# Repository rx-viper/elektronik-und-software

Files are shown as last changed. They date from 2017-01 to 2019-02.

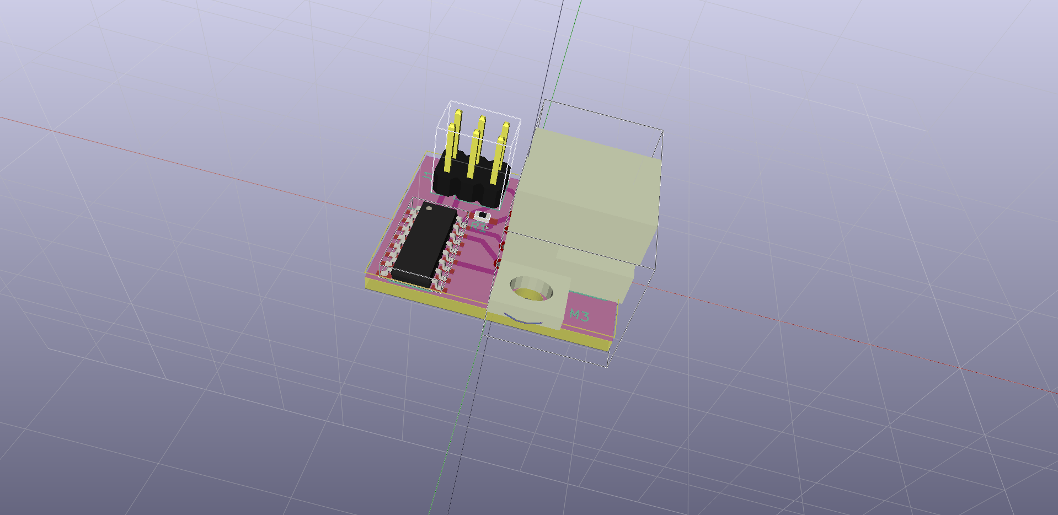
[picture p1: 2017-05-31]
boards/optical-distance/optical-distance.png

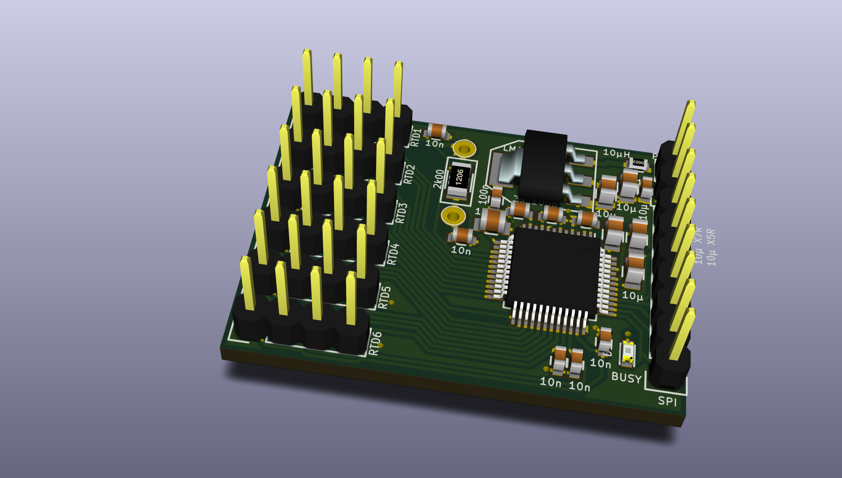
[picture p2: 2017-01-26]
docs/boards/temperature_sensor_board/ltc2984-board_3D_1.png

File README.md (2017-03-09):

# REXUS project VIPER: Elektronik and Software

### Structure of this repository

#### *boards*
* KiCAD and mechanical files for all PCBs used in the project.

#### *software/onboard*
* Code files of microcontroller software inside the rexus module.

#### *software/groundstation*
* Code files for the groundstation software (C++/Qt).

#### *docs*
* Documentation for all above.

### HowTo do changes to this repository

* Create a new branch: `git checkout -b feature/something-i-changed`
* Do your changes.
* Tell git what files your changed and want to commit: `git add my/file.changed my/other/file.changed`
* Commit your changes: `git commit -m "Description of my changes"`
* Push your changes to Github: `git push`
* Go to Github and create a new *Pull request* from your new branch to the *master* branch.
* Wait for someone to review and merge your Pull Request.
* Then checkout the *master* brach and pull the changes from Github: `git checkout master && git pull`

Use markdown syntax for text files and `*.md` file extension.

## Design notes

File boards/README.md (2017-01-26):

# rexus-viper-elektronik
Rexus Viper Elektronik Projekt

## Temperature Sensor Board
* LTC2984
* <-> 6x PT-100 4-wire
* -> 5V power supply
* <- SPI data out

## Mainboard
* -> Pressure sensor (SPI/I2C)
* -> Force sensor (analog/SPI/I2C)
* -> 5x Temperature sensor SPI (Temperature Sensor Board)
* -> Heat probe voltage and current sensing
* -> DS18B20 Temperature sensors (1-wire bus)
* 3.3V regulator
* STM32F429VI microcontroller
* Data storage (flash memory chip)
* <-> RXSM communication
* <- Raspberry Pi (UART)
* -> 5V power supply
* -> Status LEDs
* <- Control panel

## Powerboard
* -> Battery
* -> RXSM power
* 3x 60W 24V step-up converter
* <- Heat probe
* <- Motor power
* -> Motor control
* <- Battery heater
* <- Mainboard power
* <- Raspbery Pi power
* <- Camera power
* <- Camera light
* -> Camera control
* -> Heat probe control
* <- Heat probe voltage and current sensing

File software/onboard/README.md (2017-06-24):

## Onboard software

The main software is located in `src/`.
Any hardware component tests will be placed in `tests/`.

Board-specific configuration is done in `hardware_rev1.hpp` and is included from both main software and test software (`#include "../hardware_rev1.hpp` / `#include "../../hardware_rev1.hpp`).

## xpcc

To use this software you have to put a clone of the [xpcc git repository](https://github.com/roboterclubaachen/xpcc) in the same directory as this `rexus-viper-elektronik` repository.

## documentation
Documentation and flow charts can be found in docs/software/onboard folder.

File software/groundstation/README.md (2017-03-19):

## Groundstation software

#### documentation
Documentation, flow charts and and UI drafts can be found in  docs/software/groundstation folder.

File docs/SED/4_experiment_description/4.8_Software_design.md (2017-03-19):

 
## 4.8 Software design
 
### 4.8.1 Purpose
We use a Raspberry Pi compute module to handle the camera data and a powerful
microcontroller for data acquisition, experiment control and communication with RXSM.
All data shall be saved locally. Furthermore, all data except the camera data
shall be sent to ground station via RXSM.

### 4.8.2 Design
#### 4.8.2.1 Microcontroller
As you can see at the flowchart the main experiment control actions are triggered by the RXSM events.
Because of the different requirements about data acquisition we use different frequencycs for this. For details see data acquisition frequency table and data storage flowchart.
If we did not send any data in the past second, we will send an "alive" signal to check the connection state (especially for testing).
We will not control the heat probes to constant temperature, they will run on constant power, like couched at the requirements. In case of over temperature we will switch off the heat probes and switch on again with an hysteresis when cooled down enough.
Our software has a test mode, so the heat probes will not be activated while testing.
The uplink will only be used while testing to activate the test mode.
All data and also command and event log shall be sent to ground station via RXSM and be stored locally on a flash chip after LO.
For data package design see table xyz.

#### 4.8.2.2 Raspberry Pi 
The Raspberry Pi compute module, which handles the camera data, will remote controlled by the microcontroller.

#### 4.8.2.3 Groundstation
The groundstation software shall get the downstream from RXSM to store and visualize the data. 
It will have a easy to use GUI with a general log, where all incomming data will be logged and a critical log, to get a simple overview about critical events, like LO or problems like heat probe over temperature.
The GUI will visualize (in diagrams):
* the temperature distribution inside the ice cylinders
* the development of pressure
* the development of move distance and force of heat probes

It will display the connection status and will have a button to set the experiment in test mode.

### 4.8.3 Implementation
#### 4.8.3.1 Microcontroller
The microcontroller we want to use is a STM32 (see electronics). For development, we want to use C++ with the XPCC framework, it is very useful for hardware abstraction and parallelization and well known by Raphael Lehmann, who already contributed to XPCC.

#### 4.8.3.2 Raspberry Pi 
For the Raspberry Pi we want to use a minimized Linux, based on Raspbian. It will be remote controlled by the microcontroller via UART, so we don't need any complex software here.

#### 4.8.3.3 Groundstation
For the groundstation we will use C++ with QT library for graphical user interface.

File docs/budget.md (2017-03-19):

## Viper electronic budget

* Sensors
    * 100x Temperature sensor       7650..9900 €
    * 2x Pressure sensor            55 €
    * 6x Force sensor (Omega LCMKD) 3660 €
* Electronic components
    * Cameras
        * Visible light             150 €
        * IR                        250 €
    * 2x10x Batteries               80 €
    * Electronic components         1000 €
    * PCB's                         300 €
    * 2x Raspberry Pi CM3           60 €
    * Battery charger               60 €
    * Microcontroller programmer and logic analyzer 15 €
    * Cables                        150 €
    * Connectors                    350 €

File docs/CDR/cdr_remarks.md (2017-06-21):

## Electronics and SW Remarks form CDR discussion

* some double sentences and inconsistent sentences in SED
* some tbds inside SED
* some figures bottom lines are overlapping page numbers
* positioning of PCBs -> screw holes bulkhead
* we have to build boxes for every PCB, shielding very important
* no cables trough cupola wall - we need a vacuum approved connector
* RXSM connector has to be easily reachable and vertical oriented
* Simon: good schematics, could not find an error
* camera cables have to be as short as possible and shielded very well -> connect shielding to structure parts, not to PCBs GND
* some push buttons do wired things on rocket starts, select very careful
* filter motor control
* consider to use a save / arm plug for heaters
* onboard: RS-422; ground station: Rs-232
* STM should be able to check the camera status
* consider to start high frequency sampling before LO to be able to check it
* (software) test mode has to deal with LO - we will perform a full flight test at Esrange
* maybe send one timestamp at beginning and one at the end -> calculate timestamps later
* revise verification matrix software part
* batteries have to perform vacuum and vibration test
* calculate final number and power of batteries and add to SED
* batteries are a safety risk
* transportation of batteries from Esrange back is complicated
* consider check for late access status (lift mechanism really closed?)
* Esrange has a freezer for -80 deg - consider dry ice for transport, we will not be able to use our own sensors in freezer
* consider to change timeline to have more time for tests before LO
* what do we want to do in cold, what in hot CD tests?
* think about recovery -> anything special?
* error handling (flowcharts) for electrical / sw problems short before LO
* do electronics checks after switch to internal power
* for maximum packet size have a look at user manual

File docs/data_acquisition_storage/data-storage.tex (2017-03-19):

\documentclass[12pt, a4paper]{scrreprt}

\renewcommand{\familydefault}{\sfdefault}

\begin{document}

\subsubsection{Sensor data storage}
The initial idea was to store the sensor data with timestamps, but this has a few disadvantages.
\begin{itemize}
	\item Time resolution should be greater than $\frac{1}{50}s$, so we have to use milliseconds.
	\item Flight duration is 600s, but test may last longer.
	\item As a consequence 16bit timestamps are too short, we have to use 32bit timestamps (Our software framework \textit{xpcc} can handle both).
	\item A 32bit timestamp is bigger than the actual sensor data value, so it would increase the bandwidth and storage capacity by factor two to five.
	\item We don't have to store the time because we continuously sample all sensors.
\end{itemize}

\subsubsection{Solution}
\begin{itemize}
	\item Put multiple values from one unique sensor in a \textit{packet}, which also stores information about the sensor, its type and a sequence number.
	\item The packets can be used as buffers before sensor values are written to memory and transmitted.
\end{itemize}

\subsubsection{Sensor data packet}
\begin{tabular}{|c|c|c|c|}
	\hline 
	\multicolumn{3}{|c|}{\textbf{Header}} & \textbf{Payload} \\ 
	\hline 
	Sensor type & Sensor ID & Sequence Number  & Sensor values \\ 
	\hline 
	$2\,bit$ & $6\,bit$ & $4\,Byte$ & $123\,Byte$ \\ 
	\hline 
	\multicolumn{4}{|c|}{\textbf{Total packet size: 128 Byte}} \\ 
	\hline 
\end{tabular} 

\end{document}

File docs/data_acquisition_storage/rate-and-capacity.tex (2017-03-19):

\documentclass[12pt, a4paper]{scrreprt}

\renewcommand{\familydefault}{\sfdefault}

\begin{document}

\begin{tabular}{|c|c|c|c|c|}
	\hline 
	Sensor & Count & Frequency / $Hz$ & Resolution / $Byte$ & Data rate / $B/s$ \\ 
	\hline 
	Ice temperature & 27 & 1.5 & 3 & 121.5 \\ 
	\hline 
	Other temperature & 5 & $\frac{1}{10}$ & 2 & 1 \\ 
	\hline 
	HPPM force & 3 & 2 & 3 & 18 \\ 
	\hline 
	Pressure & 1 & 20 & 2 & 40 \\ 
	\hline 
	Heat probe temperature & 3 & 1.5 & 3 & 13.5 \\ 
	\hline 
	\textbf{Total} & 39 & & & 194 \\ 
	\hline 
\end{tabular} 
\\[0.5em]
Experiment duration: $120\,s \rightarrow 194B/s * 120s = 23.28kB$
\\[0.5em]
Flight duration: $600\,s \rightarrow 194B/s * 600s = 116.4kB$

\end{document}

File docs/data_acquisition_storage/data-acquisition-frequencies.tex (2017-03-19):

\documentclass[12pt, a4paper]{scrreprt}

\renewcommand{\familydefault}{\sfdefault}

\begin{document}

\begin{tabular}{|c|c|c|}
	\hline 
	Sensor & Low frequency & High frequency \\ 
	\hline 
	Ice temperature & $\frac{1}{3}\,Hz$ & $1.5\,Hz$ \\ 
	\hline 
	Battery/Structure temperature & $\frac{1}{10}\,Hz$ & $\frac{1}{5}\,Hz$ \\ 
	\hline 
	HPPM force & disabled & $2\,Hz$ \\ 
	\hline 
	Pressure & $5\,Hz$ & $20\,Hz$ \\ 
	\hline 
	Heat probe temperature & disabled & $1.5\,Hz$ \\ 
	\hline 
\end{tabular}

\end{document}

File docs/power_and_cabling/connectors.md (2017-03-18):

# Connectors

## List of connectors in experiment

**Where | type | number of pins | necessary**
* ISCA temperature sensors to mainboard | 2x D-SUB HD (44 + 62 pin) | 27x4 (=108), but each 6 sensors share 1 pin -> 86 pins | yes
* RXSM connector | DSUB-15 | 15 | yes
* Battery connector to powerboard | no? | 2x high-current + temperature sensors (5) | we could solder the battery to the powerboard
* powerboard to mainboard | D-SUB (HD?) 26 or 37 pin | about 20 | yes
* Coupola (sensors) to mainboard | D-SUB (HD?) | approx. 15 pins | yes
* Coupola (cameras) to Raspberry Pi CM3 board | D-SUB (HD?) | <=15 | yes
* Coupola (heat probes, light) to powerboard | D-SUB (?), multiple pins parallel | 6x high-current, 2x light | yes

## Available connectors

* D-SUB HD (high density) 15..78 pins; [Harting](http://www.harting.de/fileadmin/harting/documents/public/catalogue/interface_11_7_d/Interface_11_7_D_03_D-Sub-High-Density-Steckverbinder.pdf)
* D-SUB 9..50 pins
* high current: D-SUB multiple pins parallel

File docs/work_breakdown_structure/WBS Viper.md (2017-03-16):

* Specify hardware design
    * Sensors
    * Actuators
    * Batteries
    * Processing units
    * Data acquisition
    * Developing schematics
        * Calculate
        * Draw
* Specify software design
    * Requirements
    * Flow charts
* Select parts
* Develop hardware
    * Design board layouts
* Develop software
    * Ground Station
        * Telemetry data
            * Store
            * Process
            * Visualize
        * Telecommand
    * Onboard
        * Process ground commands
        * Control
            * Actuators
                * Range limit
            * Heat probes
                * Over-heating protection
            * Locking mechanism
            * Start/Stop experiment/data acquisition
            * Camera
        * Data management
            * Read sensor data
            * Store data
            * Pack and format data
            * Send to RXSM for transmission
* Assemble hardware
    * Assemble boards
    * Assemble cables
* Testing hardware components
    * Sensors
        * Temperature
        * Pressure
        * Force
        * Camera
    * Batteries
        * Vacuum
        * Temperature development under load
        * Capacity under load
        * Voltage, current at different temperatures
    * Actuators
        * Motor
        * Heat probes
* Final Assembly
    * Temperature sensors
    * Wiring
    * Adjust camera
* Final testing

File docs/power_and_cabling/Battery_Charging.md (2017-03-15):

# Battery charging

We use a 8 cell NiMH battery inside our module.

The battery is charged inside the experiment module through the RXSM charge line, which provides 1A at 28V. Our Battery is charged with 20W.

The battery charge controller is integrated to the *Powerboard* and can be enabled from the Mainboards microcontroller.
A charge status feedback is provided to the microcontroller, too.

For efficiency reasons we use the [Linear LTC4010](http://www.linear.com/product/LTC4010) *High Efficiency Standalone Nickel Battery Charger*. This integrated circuit provides reliable and safe battery charging with only a few additional components.

### Charge current
The charge current is set to 2A according to the [LTC4010s datasheet](http://cds.linear.com/docs/en/datasheet/4010fb.pdf).
```
R_sense = 100mV / I_charge
0.05 ohms = 100mV / 2A
```

### Battery cut-off
The battery is always disconnected from the load while RXSM power is not available.
For technical reasons the charging circuit is not disconnected, but is only enabled and active while the RXSM charge line is powered.
To charge the battery both RXSM power line and charge line have to be powered on because the microcontroller must enable the battery charging circuit.

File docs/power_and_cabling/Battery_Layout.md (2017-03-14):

# Battery Power and Energy Calculation
```
Heatprobes:     P = 35W + 70W + 70W + 5W margin = 180W
                U = 24V
Experiment:     t = 3min = 180s = 0,05h
Efficienty:     Step Up = 0,93
BK250 SCH       Q = 2800mAh
                m = 57g
```				
## Calculation:
```			
                    Conversation losses: 180W * 0,07 = 12,6W
                    E_Heatprobe = 180W * 0,05h = 9Wh
                    E_Cell = 1,2V * 2800mAh = 3,36Wh per Cell
                    E_Waste = 12,6W * 0,05h = 0,63Wh
                    E_total = 9Wh + 0,63Wh = 9,63Wh
    Amount Cells:   E_total/E_Cell = 9,63Wh/3,36Wh = 2,866 Cells
                    => 3 Cells

    1,1V at 20A     P_Cell = 1,1V * 20A = 22W
    (Batterychart)  P_Heatprobe = 180W
                    P_Loss = 12,6W
                    P_Total = P_Heatprobe + P_Waste = 180W + 12,6W = 192,6W
    Amount Cells:   P_Total/P_Cells = 192,6W/22W = 8,75 Cells
                    => 9 Cells

    1,0V at 30A     P_Cell = 1,0V * 30A = 30W
    (Batterychart)  P_Heatprobe = 180W
                    P_Waste = 12,6W
                    P_Total = 192,6W
    Amount Cells:   P_Total/P_Cells = 192,6W/30W = 6,41 Cells
                    => 7 Cells

    => Amount Cells chosen: 8 Cells
```

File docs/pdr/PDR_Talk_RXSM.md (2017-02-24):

## RXSM

### Telemetry
* `19.2 kbit/s` shared
* Ground station (GS) is connected to *SCIENCE-NET*
    * via RS232
    * **or:** direct TCP connection to a dedicted port at serial port server
    * we should implement both, RS232 as falllback
* Telemetry has forward error correction (FEC)
* Telemetry imput: raw serial datastream via RS422
* <64 bytes at a time
* fragmentation -> delay up to ~4ms
* RS422 termination resistor

### Signals
* LO: lift off (fixed, shared for all experiments)
* SOE: start of experiment
* SODS: start of data storage
* SOE, SODS programmable via timeline after liftoff
* SOE, SODS manually activatable before LO
* open collector
    * shared: diode decoupled
    * "active low"
    * max. 50mA
    * unstable after power on -> wait 5 seconds after power on
    * glitches are possible -> debouncing
    * use optocoupler, no anitparallel diode, e.g. PC3H7, connect direct to 28V line
* we need a special rundown sequence because of mechanical state

### Uplink
* only available before LO on RX23 (our rocket)
* use for testing, etc.

## RXSM Power
* resetable fuses in RXSM
    * >3A for >500ms
    * >15A for >10ms
    * -> no own fuses
* max. ripple voltage: 100mV_pp
* 28V nominal voltage
    * on ground: regulated 28V power supply, but long wires -> high inductance
    * during flight: unregulated battery voltage
    * total range: 24V to 36V
* provide good access to power connectors!
* power input:
    * <100µF input capacity
    * EMI supression input filter
    * 100nF at input after filter
    * GND shorted to structure only at one input point

## Cables
* 4A / mm²

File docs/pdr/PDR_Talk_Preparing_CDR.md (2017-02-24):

## CDR
* final design!
* 20 minutes presentation
* SED deadline: 22/05
* Soldering course (?)

### How to prepare:
* Use PDR feedback
* Ask! (Mail, Telefone)
* RTFM!!!

### Electronics:
* schematics
* pcb (layouts)
* Cabling!
* everything tested

### Software:
* testing subsystems
* ground station
* software responsible person must be at CDR

### Handling:
* Storage space -> read data and clear flash?

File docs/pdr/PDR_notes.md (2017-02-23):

* LO, SOE, SODS signal
* Termination resistor
* Galvanic isolation
* Battery charging through RXSM charge line
* Battery cut-off
* Late access procedure (radio silence / no power)
    * -> no LEDs
* Camera
    * EMV
    * Don*t use CSI connectors from RPi camera
    * Camera lens heater

* SED:
    * We will use LaTeX
    * verifcation is missing
    * Software Design in SED
    * Citations in SED

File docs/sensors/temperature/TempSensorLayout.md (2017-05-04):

# Configuration temperature sensors

## Calculation of accuracy

Requirements:
```
dT = 0.5°C in a range of -80°C to 0°C
dT = 0.1°C in a range of -80°C to 0°C if possible
```

#### Class B
```
dT = ± (0.30°C + 0.005 * |T|)
dT = ± (0.7°C)
```

#### Class A
```
dT = ± (0.15°C + 0.002 * |T|)
dT = ± (0.31°C)
```

#### Class AA
```
dT = ± (0.10°C + 0.0017 * |T|)
dT = ± (0.236°C)
```

#### Class 1/10 B
```
dT = ± (0.1*(0.30°C + 0.005 * |T|)
dT = ± (0.07°C)
```

=> Class A and AA fulfill the requirement, Class 1/10 B would be great

### Quantity
* 9 sensors per iceblock
* 27 sensors per ISCA
* We have two ISCAs in reserve, one for the flight. 
* 81 sensors are necessary
    * We will order 100 sensors, 81 mounted, 19 for testing and replacement

### Costs

Sensors by Omega can be custom made.
A sensor that might fit would be *P-M-1/10-2-5-M6x1* for 99€ each.

This sensor and alternatives will be discussed (PT100; 1/10 Class B; 2mm diameter; 5mm length; M6-1 screw mount).

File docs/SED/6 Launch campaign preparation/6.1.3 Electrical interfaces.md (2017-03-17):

### 6.1.3 Electrical Interfaces
#### REXUS Electrical Interfaces
* Service module interface required? Yes
    * Number of service module interfaces: 1
    * TV channel required?: No
* Downlink required? Yes
    * Data rate downlink: 20 kbit/s
* Uplink required? Yes, but only on ground
    * Data rate uplink: < 1 kbit/s
* Power system: Service module power required? Yes
    * Peak power consumption: 30 W
    * Average power consumption: 10 W
    * Total power consumption after lift-off (until T+600s): 1.67 Wh
    * Power ON: 600 s before lift-off
    * Power OFF: 600 s after lift-off
    * Battery recharging through service module: Yes
* Experiment signals: Signals from service module required? Yes
    * LO: Yes
    * SOE enable: 80 s after lift-off (begin of µg-phase)
    * SOE disable: 200 s after lift-off (end of µg-phase)
    * SODS enable: 300 s before lift-off
    * SODS disable: 550 s after lift-off (50 s before shut-down)

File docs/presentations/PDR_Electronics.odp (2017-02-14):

## Electronics

## Overview

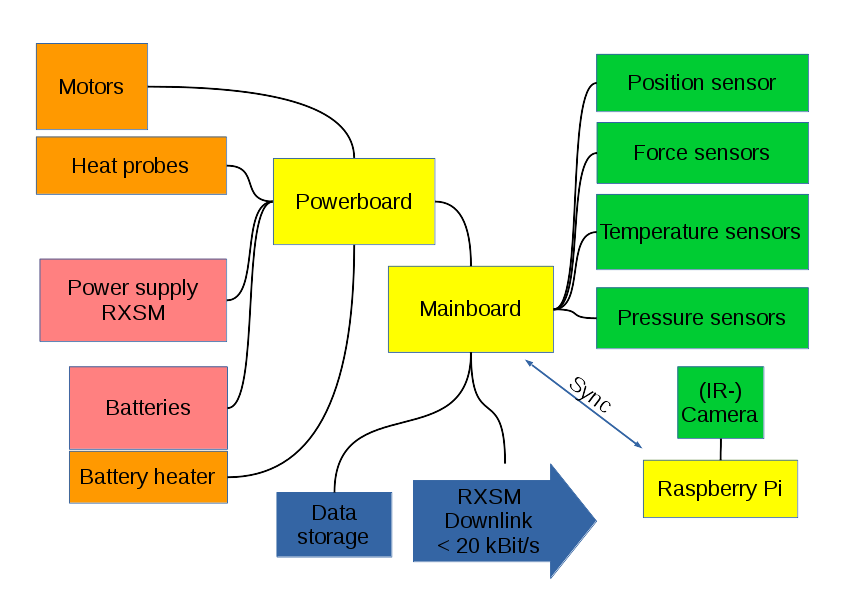
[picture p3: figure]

## Battery

- Panasonic BK300SCP
  - NiMH
  - 1.2 V
  - 3 Ah
  - 4 mΩ
- 8..10 cells
- 25..35 Wh
- Temperature monitoring
- Battery heater

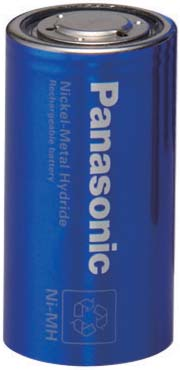
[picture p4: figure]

## Temperature Sensor Board

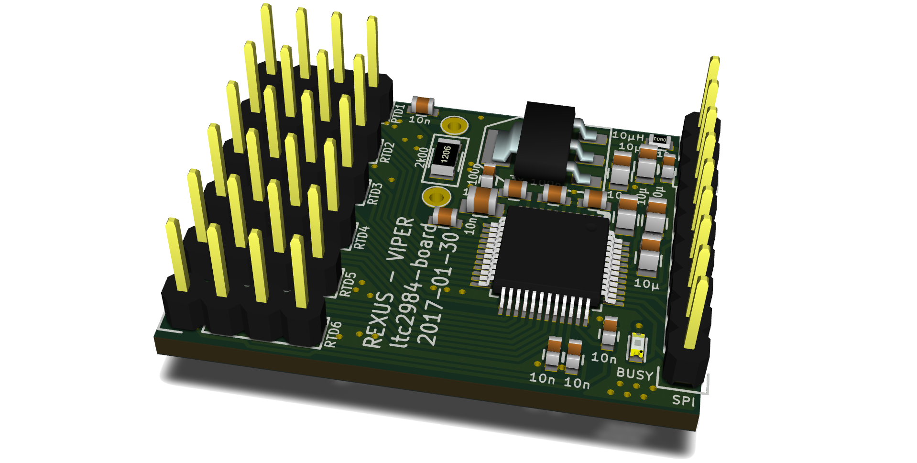
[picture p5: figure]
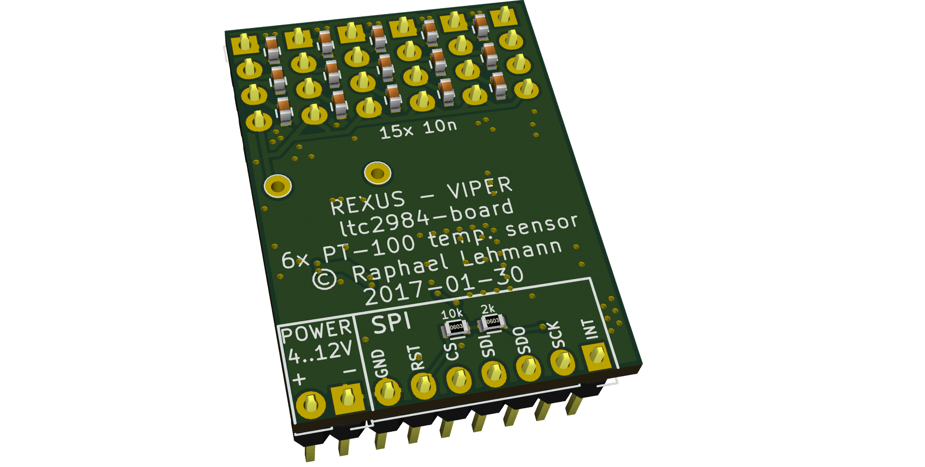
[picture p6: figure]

## Boost regulator test board

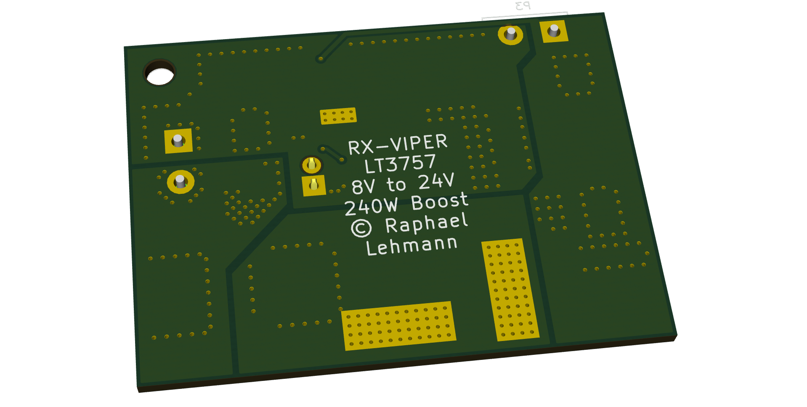
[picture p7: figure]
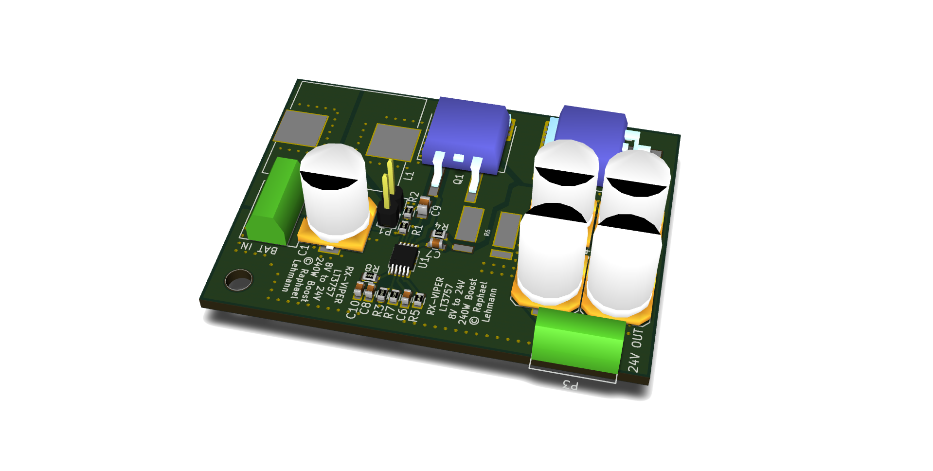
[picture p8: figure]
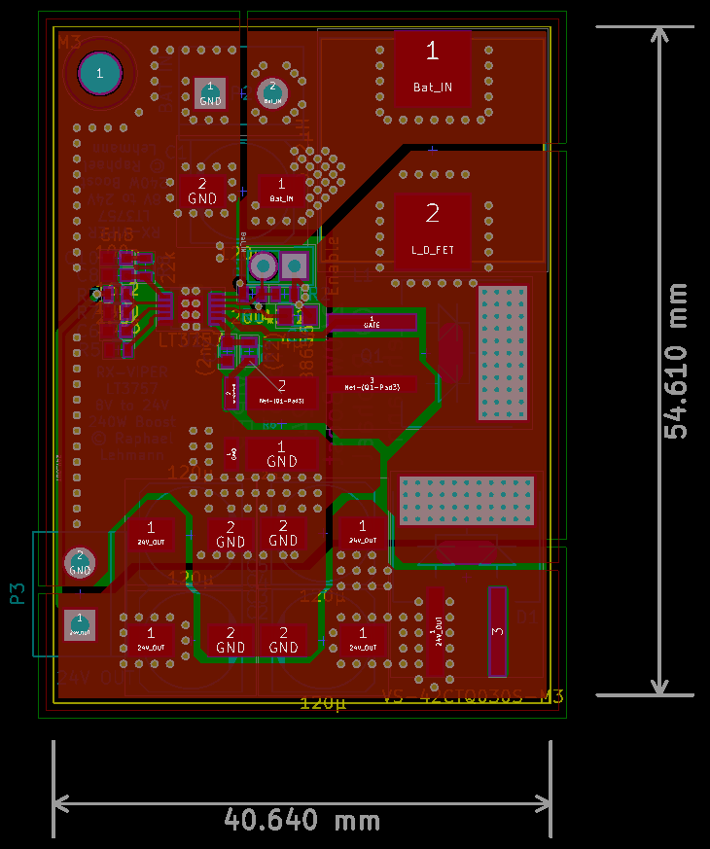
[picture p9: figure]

## Software Design

## Onboard Software

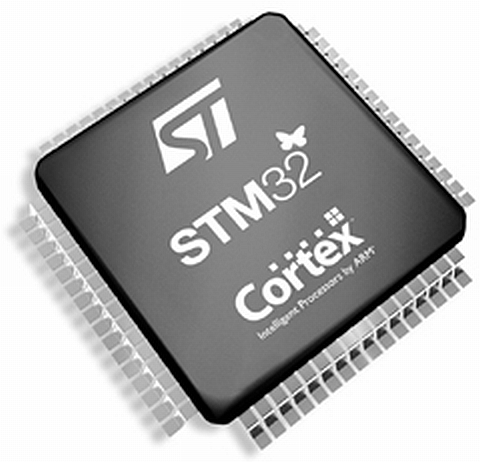
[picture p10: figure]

- STM32 microcontroller
- xpcc framework
  - C++
  Raspberry Pi: Linux
  Communication:
- xpcc
- Experiment ↔ ground station

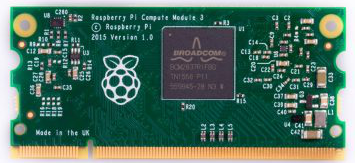
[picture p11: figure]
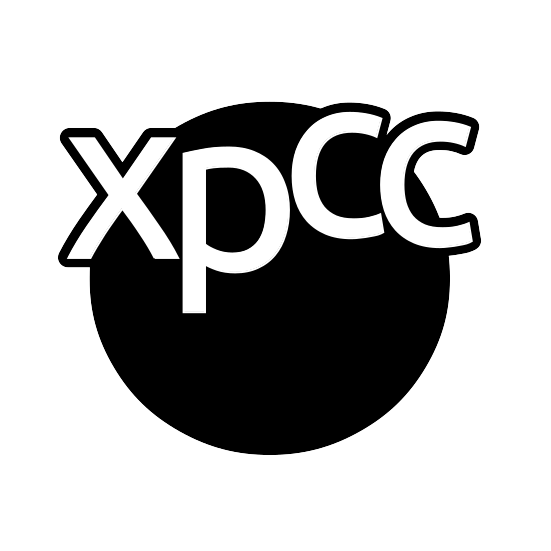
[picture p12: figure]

## Software Flowchart

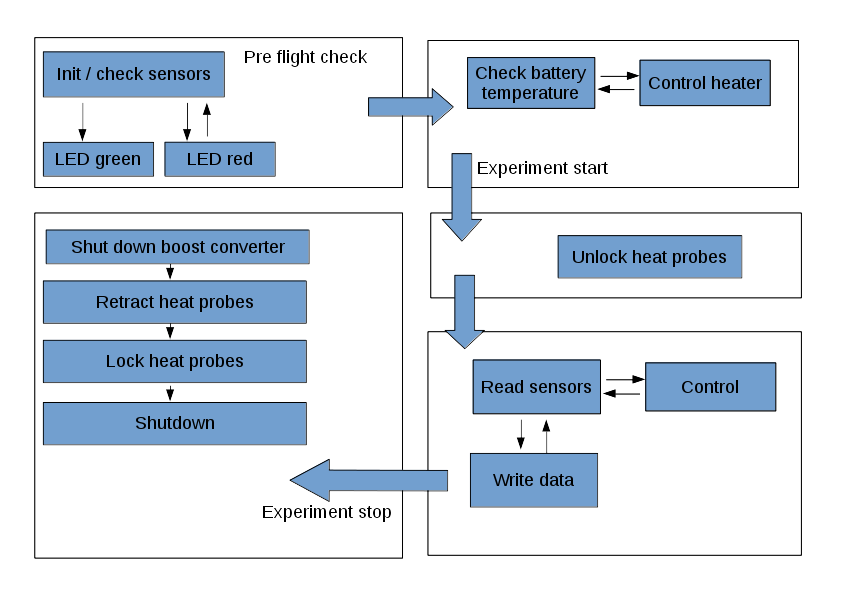
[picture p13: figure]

## Ground Station

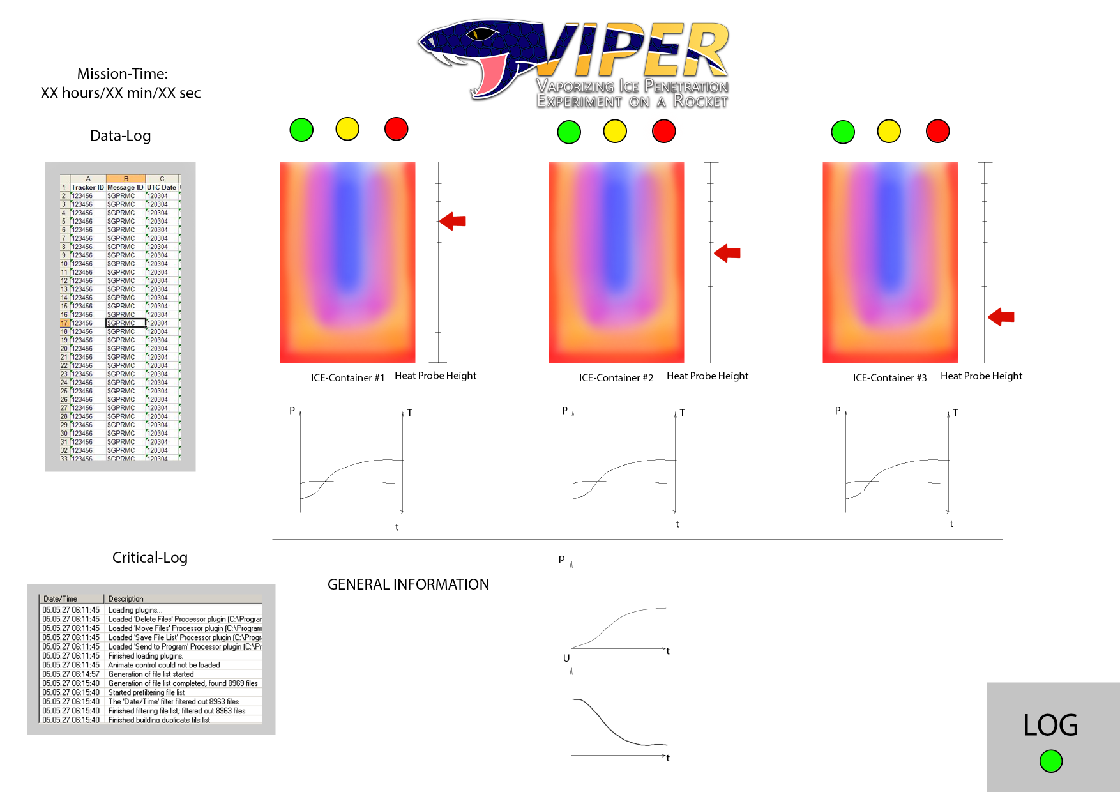
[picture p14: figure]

- Experiment status overview
- Record received data
- Qt GUI (C++)

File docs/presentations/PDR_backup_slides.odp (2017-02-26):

## Pressure sensor

- AMS 5915-0010-D
- I²C
- differential, 0..10mbar
- temperature compensated -25..85°C
- available, 25€

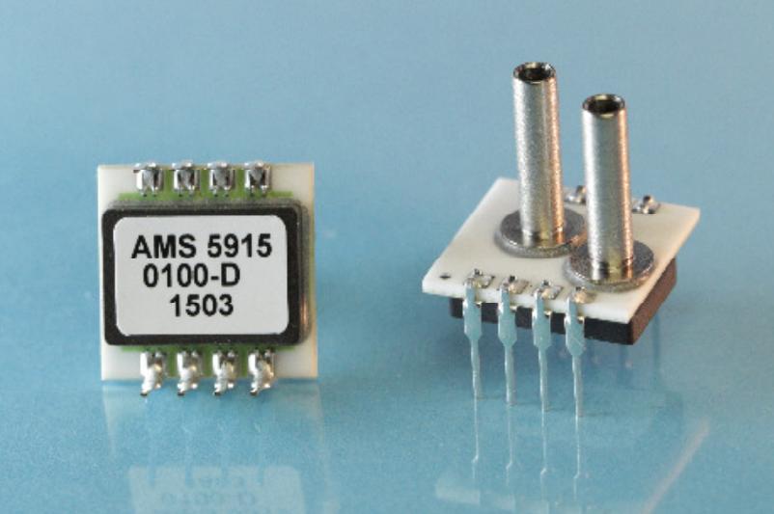
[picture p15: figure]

## Temperature sensing

- Requirement
  - Accuracy 0.5% or better
  - Range: -100°C .. 20°C
- PT-100
- LTC2984 integrated temperature measurement system
- 4-wire connections

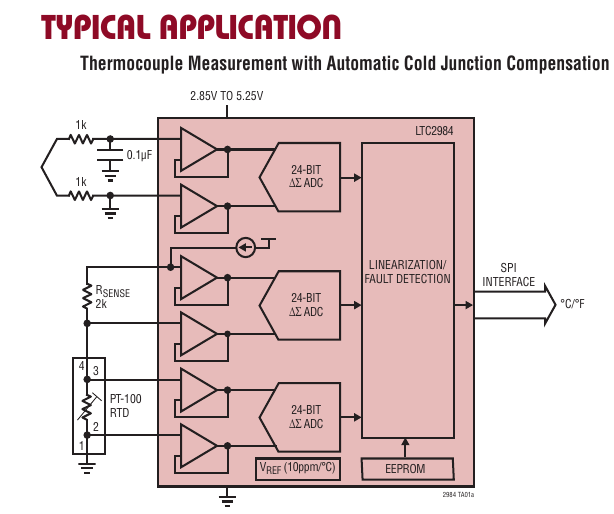
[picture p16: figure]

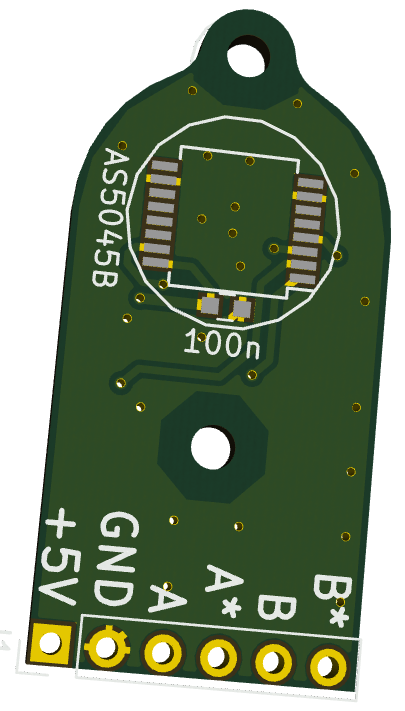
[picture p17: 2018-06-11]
docs/boards/Cupola-Boards/Renderings/Encoder-Board-VarA_Back.png

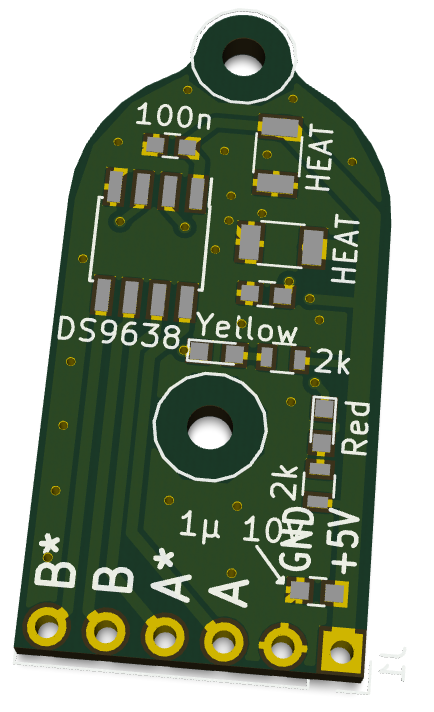
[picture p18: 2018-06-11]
docs/boards/Cupola-Boards/Renderings/Encoder-Board-VarA_Front.png

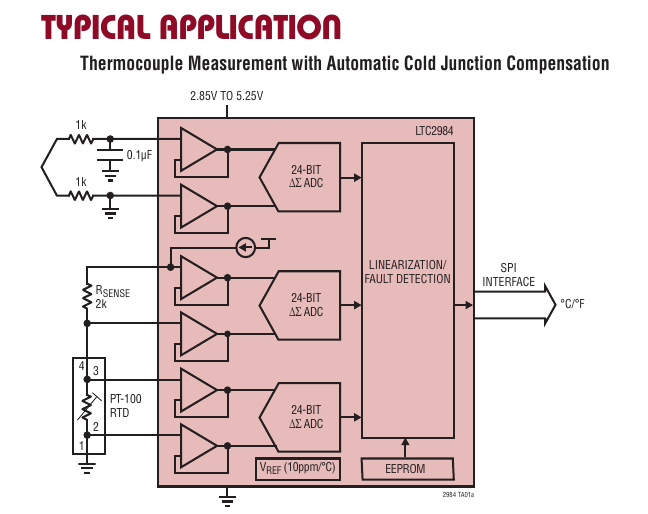
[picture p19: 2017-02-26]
docs/presentations/ltc2984-example.png

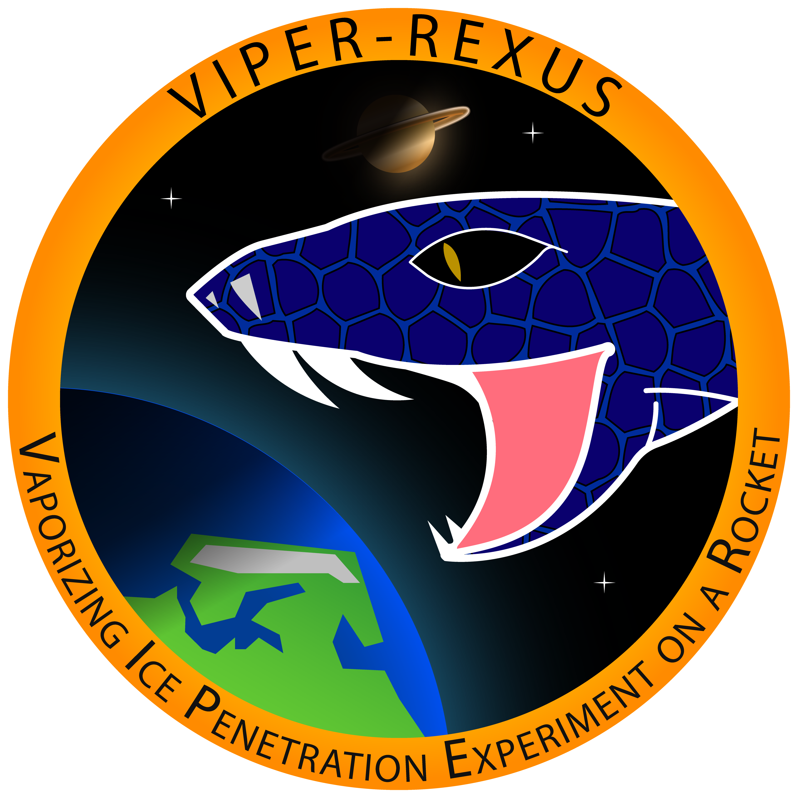
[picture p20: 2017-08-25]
docs/wires/VIPEREmblemTransparent.png

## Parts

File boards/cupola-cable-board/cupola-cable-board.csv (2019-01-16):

ID | Bezeichner | Gehäuse | Stückzahl | Bezeichnung | Anbieter und Referenz
1 | IC2,IC1 | SOIC-16_3.9x9.9mm_P1.27mm | 2 | AM26C31M
2 | J3 | PinHeader_2x03_P2.00mm_Vertical | 1 | ENC1_OUT
3 | J2 | PinHeader_2x03_P2.00mm_Vertical | 1 | ENC0_OUT
4 | J4 | PinHeader_2x03_P2.00mm_Vertical | 1 | ENC2_OUT
5 | C9,C4,C8,C10,C3,C5,C6,C11 | C_0603_1608Metric | 8 | 100n
6 | X1 | Oscillator_SMD_SeikoEpson_SG8002LB-4Pin_5.0x3.2mm | 1 | ECS-3963-120-AU-TR
7 | TP3,TP1,TP2 | TestPoint_Pad_D1.5mm | 3 | TestPoint
8 | R8,R6,R5 | R_0805_2012Metric | 3 | HEAT
9 | J5 | PinHeader_1x06_P2.00mm_Vertical | 1 | Sensor0
10 | J10 | PinHeader_1x04_P2.00mm_Vertical | 1 | MagnetEncoder2
11 | J1 | PinHeader_1x02_P2.00mm_Vertical | 1 | LED
12 | J9 | PinHeader_1x04_P2.00mm_Vertical | 1 | MagnetEncoder1
13 | J8 | PinHeader_1x04_P2.00mm_Vertical | 1 | MagnetEncoder0
14 | J7 | PinHeader_1x06_P2.00mm_Vertical | 1 | Sensor2
15 | J6 | PinHeader_1x06_P2.00mm_Vertical | 1 | Sensor1
16 | JP2 | SolderJumper-3_P1.3mm_Open_RoundedPad1.0x1.5mm | 1 | Enc0_B
17 | C2,C12,C13,C1 | C_0603_1608Metric | 4 | 1u
18 | C7 | C_0805_2012Metric | 1 | 4u7
19 | J11 | PinHeader_1x03_P2.54mm_Vertical | 1 | SWD
20 | JP1 | SolderJumper-3_P1.3mm_Open_RoundedPad1.0x1.5mm | 1 | Enc0_A
21 | JP3 | SolderJumper-3_P1.3mm_Open_RoundedPad1.0x1.5mm | 1 | Enc1_A
22 | JP4 | SolderJumper-3_P1.3mm_Open_RoundedPad1.0x1.5mm | 1 | Enc1_B
23 | JP5 | SolderJumper-3_P1.3mm_Open_RoundedPad1.0x1.5mm | 1 | Enc2_A
24 | JP6 | SolderJumper-3_P1.3mm_Open_RoundedPad1.0x1.5mm | 1 | Enc2_B
25 | U2 | LQFP-48_7x7mm_P0.5mm | 1 | STM32F410CBTx
26 | U1,U3 | SOT-23-5 | 2 | TLV75533PDBV
27 | R7,R1 | R_0603_1608Metric | 2 | 0
28 | R2,R3,R4 | R_0603_1608Metric | 3 | 3k3
29 | D1,D2,D3 | LW_G6SP_Handsoldering | 3 | LED

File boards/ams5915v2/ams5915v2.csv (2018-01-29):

Id | Designator | Package | Quantity | Designation | Supplier and ref | partsbox
1 | REF**,REF**,REF** | MountingHole_3.2mm_M3 | 3 | MountingHole_3.2mm_M3 |  | n
2 | C1,C7,C8 | C_0805 | 3 | 1u |  | x
3 | C2 | C_1206 | 1 | 10u |  | x
4 | C3,C4,C5,C6 | C_0603 | 4 | 100n |  | x
5 | D1 | LED_0603 | 1 | LED_5v |  | x | green
6 | D2 | LED_0603 | 1 | LED_3v3 |  | x | yellow
7 | D3 | LED_0603 | 1 | LED_P1 |  | x | red
8 | D4 | LED_0603 | 1 | LED_P2 |  | x | red
9 | J1 | Pin_Header_Angled_1x04_Pitch2.54mm | 1 | Conn_01x04 |  | n
10 | R1,R2 | R_0603 | 2 | 100 |  | x | Zero-ohm
11 | R3 | R_0603 | 1 | 4k7 |  | x
12 | R4,R6,R8 | R_0603 | 3 | 2k7 |  | x
13 | R5,R7 | R_0603 | 2 | 576k |  | x
14 | TP2 | Measurement_Point_Round-SMD-Pad_Small | 1 | GND |  | n
15 | TP3 | Measurement_Point_Round-SMD-Pad_Small | 1 | 3v3 |  | n
16 | U1 | SOT-23-5 | 1 | TLV73333PDBVR |  | x
17 | U2,U4 | SOT-23-6 | 2 | MAX4995A |  | x
18 | U3,U5 | AMS_5915-XXXX-D_differential_pressure_sensor | 2 | AMS5915 |  | x
19 | TP1 | Measurement_Point_Round-SMD-Pad_Small | 1 | 5v |  | n

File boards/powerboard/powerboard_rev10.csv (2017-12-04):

ID | Bezeichner | Gehäuse | Stückzahl | Bezeichnung | Anbieter und Ref. | partsbox
1 | J113,J112,J113,J114,J115,J117 | MountingHole_3.2mm_M3_Pad | 6 | M3 |  | n
2 | C503 | C_0805 | 1 | 10µ 0805 35V |  | 1 | 0
3 | FL101,FL102 | WE-SL5 | 2 | 744272471 |  | 2 | 0
4 | C104,C505 | C_0805 | 2 | 10µ |  | 2 | 0
5 | C105,C304,C305,C308,C309,C310,C312,C315,C504,C701,C801,C802,C803,C901,C902,C1002,C109,C506,C1201,C1202,C302,C306 | C_0603 | 22 | 100n |  | 22 | 0
6 | C106 | C_0805 | 1 | 470n |  | 1 | 0
7 | C201 | C_1206 | 1 | 10µ/40V |  | 1 | 0
8 | C202 | C_0805 | 1 | 1µ/40V |  | 1 | 0
9 | C203,C204 | C_0603 | 2 | 22n |  | 2 | 0
10 | C205,C110,C111,C112,C113,C114,C115,C116,C117,C910,C911,C912,C913,C914,C915,C916,C917 | C_0603 | 17 | 10n |  | 17 | 0
11 | C303 | C_0603 | 1 | 10µ |  | 1 | 0
12 | C307,C314,C702,C1001,C207 | C_0603 | 5 | 1µ |  | 5 | 0
13 | C313 | C_0603 | 1 | 4µ7 0805 |  | 1 | 0
14 | C316,C317,C318 | C_0603 | 3 | 100p |  | 3 | 0
15 | C501 | C_0603 | 1 | 68n |  | 1 | 0
16 | C502 | C_0603 | 1 | 47n |  | 1 | 0
17 | C1101,C1102,C1103,C1104,C1105,C1106,C1107,C1108,C1109,C1110,C1111,C1112,C1113,C1114,C1115,C1116,C508 | C_0603 | 17 | 220n |  | 17 | 0
18 | D301,D302 | LED_0603 | 2 | LED |  | 2 | 0
19 | D701,D702 | SOT-23 | 2 | ESD |  | 2 | 0
20 | J102 | Pin_Header_Straight_2x20_Pitch2.54mm | 1 | Powerboard <-> Mainboard |  | 0 | 1
21 | J105 | MountingHole_3.2mm_M3_Pad_Via | 1 | BOOST |  | 0 | 1
22 | J106 | Pin_Header_Straight_1x01_Pitch2.54mm | 1 | Boost24V_EN |  | 0 | 1
23 | J107 | MountingHole_3.2mm_M3_Pad_Via | 1 | 24V_1 |  | 0 | 1
24 | J108 | MountingHole_3.2mm_M3_Pad_Via | 1 | 24V_2 |  | 0 | 1
25 | J109 | MountingHole_3.2mm_M3_Pad_Via | 1 | 24V_3 |  | 0 | 1
26 | J110 | MountingHole_3.2mm_M3_Pad_Via | 1 | BAT |  | 0 | 1
27 | J111 | MountingHole_3.2mm_M3_Pad_Via | 1 | GND |  | 0 | 1
28 | L301,L302,L303 | L_1812 | 3 | 742792515 |  | 3 | 0
29 | Q101 | TO-263-3Lead | 1 | SQM40031EL |  | 1 | 0
30 | Q102 | SOT-23 | 1 | DMN6140L |  | 1 | 0
31 | Q104 | SOT-23 | 1 | PMV55ENEA |  | 1 | 0
32 | Q503 | SOIC-8_3.9x4.9mm_Pitch1.27mm | 1 | IRF7343PBF |  | 1 | 0
33 | Q801,Q802,Q803 | SOT-669_LFPAK | 3 | BUK7Y4R8-60E |  | 3 | 0
34 | R101,R103,R801,R802,R803,R125,R126,R807,R808,R809,R508,R123,R124,R128 | R_0603 | 14 | 10k |  | 14 | 0
35 | R102 | R_0603 | 1 | 20k |  | 1 | 0
36 | R104 | R_0603 | 1 | 91k |  | 1 | 0
37 | R105 | R_0603 | 1 | 13k |  | 1 | 0
38 | R106,R108,R113 | R_0603 | 3 | 15k |  | 3 | 0
39 | R107,R109,R110,R111,R114,R607,R608,R130 | R_0603 | 8 | 1k |  | 8 | 0
40 | R112,R1002,R129 | R_0603 | 3 | 100k |  | 3 | 0
41 | R201 | R_0603 | 1 | 68k1 |  | 1 | 0
42 | R202 | R_0603 | 1 | 11k8 |  | 1 | 0
43 | R203 | R_0603 | 1 | 43k2 |  | 1 | 0
44 | R204 | R_0603 | 1 | 5k62 |  | 1 | 0
45 | R205 | R_0603 | 1 | 1k07 |  | 1 | 0
46 | R301,R302 | R_0603 | 2 | 470 |  | 2 | 0
47 | R303 | R_0603 | 1 | 200k |  | 1 | 0
48 | R504 | R_0603 | 1 | 65k7 |  | 1 | 0
49 | R505 | R_0603 | 1 | 8k2 |  | 1 | 0
50 | R506 | R_0603 | 1 | 50k |  | 1 | 0
51 | R1001 | R_0603 | 1 | 140k |  | 1 | 0
52 | R1003 | R_0603 | 1 | 4k7 |  | 1 | 0
53 | R1004 | R_0603 | 1 | 2R |  | 1 | 0
54 | R1101,R1102,R1103,R1104,R1105,R1106,R1107,R1108,R1109,R1110,R1111,R1112,R1113,R1114,R1115,R1116 | R_0603 | 16 | 47k |  | 16 | 0
55 | U102 | SOIC-16_3.9x9.9mm_Pitch1.27mm | 1 | DS26LV32AT |  | 1 | 0
56 | U201 | 7TO-PMOD | 1 | LMZ14203 |  | 1 | 0
57 | U302 | HSSOP-36 | 1 | DRV8332 |  | 1 | 0
58 | U303,U801,U802,U803 | SOIC-8_3.9x4.9mm_Pitch1.27mm | 4 | ACS711 |  | 4 | 0
59 | U501 | TSSOP-16-1EP_4.4x5mm_Pitch0.65mm | 1 | LTC4010 |  | 1 | 0
60 | U601,U602,U603 | SOP-4 | 3 | PC3H7 |  | 3 | 0
61 | U701 | SOIC-14_3.9x8.7mm_Pitch1.27mm | 1 | MAX13432EESD |  | 1 | 0
62 | U901 | TSSOP-20_4.4x6.5mm_Pitch0.65mm | 1 | AD7928 |  | 1 | 0
63 | U902 | SOT-23 | 1 | REF3025 |  | 1 | 0
64 | U1001 | MSOP-10-1EP_3x3mm_Pitch0.5mm | 1 | LT3592 |  | 1 | 0
65 | U1101,U1102 | TSSOP-14_4.4x5mm_Pitch0.65mm | 2 | LMV324 |  | 2 | 0
66 | C103 | C_0805 | 1 | 1µ |  | 1 | 0
67 | L101 | L_Coilcraft_1583_Handsoldering | 1 | Coilcraft MSS1583-474 |  | 1 | 0
68 | L501 | L_Coilcraft_XAL60xx_Handsoldering | 1 | Coilcraft XAL6060-223 |  | 1 | 0
69 | L1001 | L_Coilcraft_XAL40xx_Handsoldering | 1 | Coilcraft XAL4040-103 |  | 1 | 0
70 | U101 | SOT-223 | 1 | LM1117-3.3 |  | 1 | 0
71 | R115,R116,R117,R118,R120 | R_0603 | 5 | NC |  | 0 | 5
72 | FL701,FL702 | WE-SL2 | 2 | CMC |  | 2 | 0
73 | C319,C804,C805,C806 | C_0603 | 4 | 1n |  | 4 | 0
74 | R122 | R_0603 | 1 | 0 |  | 1 | 0
75 | J101 | DB15MD | 1 | RXSM experiment connector |  |  | 1
76 | J103 | DB9FD | 1 | Cameraboard |  |  | 1
77 | J104 | DB15FD | 1 | BLDC Motor |  |  | 1
78 | J810 | MountingHole_3.2mm_M3_Pad_Via | 1 | HP1 |  |  | 1
79 | J811 | MountingHole_3.2mm_M3_Pad_Via | 1 | HP2 |  |  | 1
80 | J812 | MountingHole_3.2mm_M3_Pad_Via | 1 | HP3 |  |  | 1
81 | D101 | LED_0603 | 1 | RX-PW |  | 1 | 0
82 | D102 | LED_0603 | 1 | RX-CHG |  | 1 | 0
83 | D103 | LED_0603 | 1 | BAT |  | 1 | 0
84 | D801 | LED_0603 | 1 | HP1 |  | 1 | 0
85 | D802 | LED_0603 | 1 | HP2 |  | 1 | 0
86 | D803 | LED_0603 | 1 | HP3 |  | 1 | 0
87 | R127 | R_0603 | 1 | 4k |  | 1 | 0
88 | TP101 | Measurement_Point_Round-SMD-Pad_Small | 1 | 28V |  |  | 1
89 | TP102 | Measurement_Point_Round-SMD-Pad_Small | 1 | CHG |  |  | 1
90 | TP103 | Measurement_Point_Round-SMD-Pad_Small | 1 | +5V |  |  | 1
91 | TP104 | Measurement_Point_Round-SMD-Pad_Small | 1 | +3V3 |  |  | 1
92 | TP105,TP106 | Measurement_Point_Round-SMD-Pad_Small | 2 | GND |  |  | 2
93 | TP107 | Measurement_Point_Round-SMD-Pad_Small | 1 | HP3C |  |  | 1
94 | TP108 | Measurement_Point_Round-TH_Small | 1 | GND |  |  | 1
95 | TP109 | Measurement_Point_Round-SMD-Pad_Small | 1 | HP2C |  |  | 1
96 | TP110 | Measurement_Point_Round-SMD-Pad_Small | 1 | HP1C |  |  | 1
97 | TP111 | Measurement_Point_Round-SMD-Pad_Small | 1 | V_MOTOR |  |  | 1
98 | TP112 | Measurement_Point_Round-SMD-Pad_Small | 1 | MOTORC |  |  | 1
99 | C101 | C_1206 | 1 | 10µ |  | 1 | 0
100 | C108 | C_1206 | 1 | 22µ Tantal |  | 1 | 0
101 | C206 | C_1812 | 1 | 100µ/10V |  | 1 | 0
102 | C301 | C_0805 | 1 | 4µ7 0805 |  | 1 | 0
103 | C507 | C_0603 | 1 | 470n |  | 1 | 0
104 | C1003 | C_0805 | 1 | 4µ7 0805 50V |  | 1 | 0
105 | D104 | D_SMB_Standard | 1 | SMAJ36A |  | 1 | 0
106 | D304,D305,D306 | D_SMB_Standard | 3 | SMBJ40CA |  | 3 | 0
107 | D501 | D_SMB_Standard | 1 | MBRS360BT3G |  | 1 | 0
108 | R507 | R_1812 | 1 | 100m |  | 1 | 0
109 | R601,R602,R603,R604,R605,R606 | R_1206 | 6 | 10k 1206 |  | 6 | 0
110 | U301 | TO-220_Vertical | 1 | 7812SR-C |  | 1 | 0
111 | U1201 | TSSOP-16_4.4x5mm_Pitch0.65mm | 1 | CD40109B |  | 1 | 0
112 | C102 | C_1206 | 1 | 4µ7 1206 50V |  | 1 | 0
113 | C118 | C_1210 | 1 | 10µ 1210 |  | 1 | 0
114 | C119 | C_0805 | 1 | 1µ 0805 50V |  | 1 | 0
115 | C120 | CP_Elec_8x10.5 | 1 | 50SVPK68M |  | 1 | 0
116 | D1001 | D_SMA_Standard | 1 | MBRA140T3 |  | 1 | 0
117 | C107,C121 | C_0603 | 2 | 2n7 |  | 2 | 0
118 | R119,R121 | R_0603 | 2 | 100 |  | 2 | 0
119 | D1002,D1003 | D_SOD-123F | 2 | US1NWF |  | 2 | 0
120 | Q103 | SOT-23 | 1 | PMV27UPE |  | 1 | 0

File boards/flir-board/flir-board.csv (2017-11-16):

ID | Bezeichner | Gehäuse | Stückzahl | Bezeichnung | Anbieter und Ref.
1 | C101,C102,C107,C108,C109 | C_0603 | 5 | 10u 25V 0603 |  | x | 5
2 | C103 | C_0603 | 1 | 1u |  | x | 2
3 | C104 | C_0805 | 1 | 10u |  | x | 1
4 | C105,C106,C113,C114,C115 | C_0603 | 5 | 100n |  | x | 5
5 | C110 | C_1206 | 1 | 10u 1206 |  | x | 1
6 | C111 | C_0603 | 1 | 1u 0603 |  | x | so
7 | C112 | C_0603 | 1 | 10n |  | x | 1
8 | D101 | D_SMB_Standard | 1 | SMBJ3V3HE3 |  | x | 1
9 | J101 | Pin_Header_Straight_1x02_Pitch2.54mm | 1 | POWER |  | no
10 | J102 | Pin_Header_Straight_1x02_Pitch2.54mm | 1 | I2C |  | no
11 | J103 | Pin_Header_Straight_1x04_Pitch2.54mm | 1 | SPI |  | no
12 | J104 | Pin_Header_Straight_1x01_Pitch2.54mm | 1 | GPIO3 |  | no
13 | L101 | L_7.3x7.3_H3.5 | 1 | SRR0603-100ML |  | x | 1
14 | R101,R102 | R_1206 | 2 | HEAT |  | no
15 | R103,R105 | R_0603 | 2 | 10k |  | x | 2
16 | R104 | R_0603 | 1 | 100k |  | x | 1
17 | U101 | SOT89-5_Housing | 1 | XC6220B281PR-G |  | x | 1
18 | U102 | SOT89-5_Housing | 1 | XC6220B301PR-G |  | x | 1
19 | U103 | SOT89-5_Housing | 1 | XC6222B121PR-G |  | x | 1
20 | U104 | Molex_105028-1001 | 1 | Flir_LEPTON |  | x | 1
21 | X101 | xt23 | 1 | ASTMHTE-25.000MHZ-ZJ-E |  | x | 1

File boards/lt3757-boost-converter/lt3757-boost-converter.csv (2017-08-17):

Id | Designator | Package | Quantity | Designation | partsbox
1 | U1 | MSOP-10-1EP_3x3mm_Pitch0.5mm | 1 | LT3757 | x
2 | L1 | Inductor_Wurth_HCI-1890 | 1 | 2.4µH | x
3 | C2,C1,C3,C4,C5 | CP_Elec_10x10.5 | 5 | 120µ | x
4 | R6 | WSLP2726 | 1 | 2m | x
5 | C6,C13,C14,C17 | C_0603_HandSoldering | 4 | 100n | x
6 | C7 | C_0603_HandSoldering | 1 | (2n2) | x
7 | C8 | C_0603_HandSoldering | 1 | 100p | x
8 | C9 | C_0805_HandSoldering | 1 | 4µ7 | x
9 | C10 | C_0603_HandSoldering | 1 | 6n8 | x
10 | C11 | C_0603_HandSoldering | 1 | (470p) | x
11 | C12 | C_0603_HandSoldering | 1 | 1µ | x
12 | C15 | C_0603_HandSoldering | 1 | 47n | x
13 | C16 | C_0603_HandSoldering | 1 | 10n | x
14 | D1 | TO-263-3Lead | 1 | VS-42CTQ030S-M3 | x
15 | J2 | Measurement_Point_Round-SMD-Pad_Small | 1 | Enable
16 | Q1 | TO-263-3Lead | 1 | FDB86566 | x
17 | R1 | R_0603_HandSoldering | 1 | 200k | x
18 | R2 | R_0603_HandSoldering | 1 | 43k2 | x
19 | R3 | R_0603_HandSoldering | 1 | 226k | x
20 | R4 | R_0603_HandSoldering | 1 | (22) | x
21 | R5 | R_0603_HandSoldering | 1 | 10k5 | x
22 | R7 | R_0603_HandSoldering | 1 | 16k2 | x
23 | R8 | R_0603_HandSoldering | 1 | 22k | x
24 | J1,J9 | MountingHole_3.2mm_M3_Pad | 2 | GND
25 | J3 | MountingHole_3.2mm_M3_Pad | 1 | BAT
26 | J4 | MountingHole_3.2mm_M3_Pad | 1 | 24V
27 | J5,J6,J7,J8 | MountingHole_3.2mm_M3_Pad | 4 | M3
28 | TP1,TP2 | Measurement_Point_Round-SMD-Pad_Small | 2 | FBX

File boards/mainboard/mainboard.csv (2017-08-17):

Id | Designator | Package | Quantity | Designation | partsbox
1 | U1201 | D-Sub_HD_26_F | 1 | Heat probe encoder
2 | U901 | TQFP-144_20x20mm_Pitch0.5mm | 1 | STM32F429ZITx | x |  | x
3 | U1101,U1001 | SOIC-8_3.9x4.9mm_Pitch1.27mm | 2 | SST26VF064B | x |  | !!!!
4 | X901 | XO53 | 1 | XO53 | x |  | x
5 | C101 | C_0603 | 1 | 1µ | x |  | x
6 | C102,C104,C105,C323,C324,C325,C423,C424,C425,C523,C524,C525,C623,C624,C625,C723,C724,C725,C823,C824,C825,C901,C902,C907,C908,C909,C910,C911,C912,C913,C914,C1001,C1101,C915,C916,C1207,C1208 | C_0603 | 37 | 100n | x |  | x
7 | C103,C106,C327,C427,C527,C627,C727,C827,C905 | C_0805 | 9 | 10µ | x |  | 15 != 21
8 | C301,C302,C303,C304,C305,C306,C307,C308,C309,C310,C311,C312,C313,C314,C315,C316,C317,C318,C319,C320,C401,C402,C403,C404,C405,C406,C407,C408,C409,C410,C411,C412,C413,C414,C415,C416,C417,C418,C419,C420,C501,C502,C503,C504,C505,C506,C507,C508,C509,C510,C511,C512,C513,C514,C515,C516,C517,C518,C519,C520,C601,C602,C603,C604,C605,C606,C607,C608,C609,C610,C611,C612,C613,C614,C615,C616,C617,C618,C619,C620,C701,C702,C703,C704,C705,C706,C707,C708,C709,C710,C712,C714,C716,C717,C718,C719,C720,C801,C802,C803,C804,C805,C806,C807,C808,C809,C810,C811,C812,C813,C814,C815,C816,C817,C818,C819,C820 | C_0603 | 117 | 10n | x |  | x
9 | C321,C421,C521,C621,C721,C821 | C_0805 | 6 | 10µ X7R | so |  | so
10 | C322,C422,C522,C622,C722,C822 | C_0805 | 6 | 10µ X5R | so |  | so
11 | C326,C426,C526,C626,C726,C826 | C_0805 | 6 | 1µ | so |  | so
12 | C903,C904 | C_0805 | 2 | 2µ2 | x |  | x
13 | C906 | C_0805 | 1 | 4µ7 | x |  | x
14 | C1201,C1202,C1203,C1204,C1205,C1206 | C_0603 | 6 | 2n7 | x |  | x
15 | D301,D401,D501,D601,D701,D801 | LED_0603 | 6 | BUSY | x | blue | x
16 | J101 | Pin_Header_Straight_2x20_Pitch2.54mm | 1 | Powerboard <-> Mainboard |  |  | x
17 | P901 | Pin_Header_Straight_1x03_Pitch2.54mm | 1 | DEBUG |  |  | x
18 | P902 | Pin_Header_Straight_1x03_Pitch2.54mm | 1 | SWD |  |  | x
19 | R101,R102,R103,R104 | R_0603 | 4 | 4k7 | x |  | x
20 | R105,R106,R107,R901 | R_0603 | 4 | 1k | x |  | x
21 | R108 | R_0603 | 1 | NC
22 | R301,R401,R501,R601,R701,R801 | R_1206 | 6 | 2k00 | x |  | x
23 | R303,R403,R503,R603,R703,R803 | R_0603 | 6 | 2k | x |  | x
24 | R304,R404,R504,R604,R704,R804 | R_0603 | 6 | 10k | x |  | x
25 | R902 | R_0603 | 1 | 560 | x |  | x
26 | R1201,R1202,R1203,R1204,R1205,R1206 | R_0603 | 6 | 0 | x |  | x
27 | R1207,R1208,R1209,R1210,R1211,R1212 | R_0603 | 6 | 2k7 | x |  | x
28 | R1213,R1214,R1215,R1216,R1217,R1218 | R_0603 | 6 | 100 | x |  | x
29 | SW101,SW102 | SW_SPST_FSMSM | 2 | SW_PUSH | x |  | x
30 | SW901 | SW_SPST_FSMSM | 1 | RESET | x |  | so
31 | SW902 | SW_SPST_FSMSM | 1 | BOOT0 | x |  | so
32 | U101 | SOT-223 | 1 | LM1117-3.3 | x |  | x
33 | U301,U401,U501,U601,U701,U801 | LQFP-48_7x7mm_Pitch0.5mm | 6 | LTC2984 | x |  | x
34 | U1202,U1203 | SOIC-16_3.9x9.9mm_Pitch1.27mm | 2 | DS26LV32AT | x |  | x
35 | D101 | LED_0603 | 1 | RED | x |  | x
36 | D102 | LED_0603 | 1 | BLUE | x |  | so
37 | D103 | LED_0603 | 1 | GREEN | x |  | x
38 | J104 | Measurement_Point_Round-SMD-Pad_Small | 1 | temp_SCL
39 | J105 | Measurement_Point_Round-SMD-Pad_Small | 1 | temp_SDA
40 | J106 | Measurement_Point_Round-SMD-Pad_Small | 1 | pres_SCL
41 | J107 | Measurement_Point_Round-SMD-Pad_Small | 1 | pres_SDA
42 | J108 | Measurement_Point_Round-SMD-Pad_Small | 1 | RasPi_TX
43 | J109 | Measurement_Point_Round-SMD-Pad_Small | 1 | RasPi_RX
44 | J110 | Measurement_Point_Round-SMD-Pad_Small | 1 | 3V3
45 | J111 | Measurement_Point_Round-SMD-Pad_Small | 1 | GND
46 | J202 | Measurement_Point_Round-SMD-Pad_Small | 1 | T_SPI1_SCK
47 | J203 | Measurement_Point_Round-SMD-Pad_Small | 1 | T_SPI1_MISO
48 | J204 | Measurement_Point_Round-SMD-Pad_Small | 1 | T_SPI1_MOSI
49 | J205 | Measurement_Point_Round-SMD-Pad_Small | 1 | T_SPI2_SCK
50 | J206 | Measurement_Point_Round-SMD-Pad_Small | 1 | T_SPI2_MISO
51 | J207 | Measurement_Point_Round-SMD-Pad_Small | 1 | T_SPI2_MOSI
52 | J208 | Measurement_Point_Round-SMD-Pad_Small | 1 | T_SPI1_CS1
53 | J209 | Measurement_Point_Round-SMD-Pad_Small | 1 | T_SPI1_CS2
54 | J210 | Measurement_Point_Round-SMD-Pad_Small | 1 | T_SPI1_CS3
55 | J211 | Measurement_Point_Round-SMD-Pad_Small | 1 | T_SPI2_CS1
56 | J212 | Measurement_Point_Round-SMD-Pad_Small | 1 | T_SPI2_CS2
57 | J213 | Measurement_Point_Round-SMD-Pad_Small | 1 | T_SPI2_CS3
58 | J1001 | Measurement_Point_Round-SMD-Pad_Small | 1 | FL2_CS
59 | J1002 | Measurement_Point_Round-SMD-Pad_Small | 1 | FL2_SCK
60 | J1003 | Measurement_Point_Round-SMD-Pad_Small | 1 | FL2_MISO
61 | J1004 | Measurement_Point_Round-SMD-Pad_Small | 1 | FL2_MOSI
62 | J1101 | Measurement_Point_Round-SMD-Pad_Small | 1 | FL1_CS
63 | J1102 | Measurement_Point_Round-SMD-Pad_Small | 1 | FL1_SCK
64 | J1103 | Measurement_Point_Round-SMD-Pad_Small | 1 | FL1_MISO
65 | J1104 | Measurement_Point_Round-SMD-Pad_Small | 1 | FL1_MOSI
66 | J1201 | Measurement_Point_Round-SMD-Pad_Small | 1 | ENC1_A
67 | J1202 | Measurement_Point_Round-SMD-Pad_Small | 1 | ENC1_B
68 | J1203 | Measurement_Point_Round-SMD-Pad_Small | 1 | ENC2_A
69 | J1204 | Measurement_Point_Round-SMD-Pad_Small | 1 | ENC2_B
70 | J1205 | Measurement_Point_Round-SMD-Pad_Small | 1 | ENC3_A
71 | J1206 | Measurement_Point_Round-SMD-Pad_Small | 1 | ENC3_B
72 | R109,R110,R111,R112,R113,R114 | R_0603 | 6 | 0R | x |  | so
73 | L101 | L_Coilcraft_XAL40xx_Handsoldering | 1 | XAL4040-153 | x |  | x
74 | J102 | DB9FD | 1 | Temperature & Pressure
75 | J103 | DB9FD | 1 | Camera board
76 | J201 | DB25FD | 1 | RTD_31-36
77 | U202 | D-Sub_HD_78_F | 1 | RTD_1-19
78 | U201 | D-Sub_HD_44_F | 1 | RTD_20-30
79 | J112,J113,J114,J115,J116,J117 | MountingHole_3.2mm_M3_Pad | 6 | M3

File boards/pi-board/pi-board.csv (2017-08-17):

Id | Designator | Package | Quantity | Designation | partsbox |  | Mouser
1 | J2 | DB25MD | 1 | Mainbord / Powerboard + Camera | n |  | n
2 | C1,C2,C3,C4,C5 | C_0603_HandSoldering | 5 | 47u | xx | 10u for 5V | 12
3 | J5 | USB_Micro-B | 1 | Bootloader | x |  | 4
4 | J7,J1,J4 | GS3 | 3 | GS3 | n |  | n
5 | C7,C11,C12 | C_0603_HandSoldering | 3 | 10u | x |  | su
6 | C9,C10 | C_0603_HandSoldering | 2 | NF | n |  | n
7 | D1 | LED_0603 | 1 | POWER | x | Red | würth
8 | D2 | LED_0603 | 1 | ACT | x | Green | würth
9 | TP1 | Measurement_Point_Round-SMD-Pad_Small | 1 | TEST_EMMC _DISABLE | n |  | n
10 | TP2,TP3,TP4 | Measurement_Point_Round-SMD-Pad_Small | 3 | TEST | n |  | n
11 | U1 | pam2306 | 1 | PAM2306 | x |  | 4
12 | L1,L2 | Inductor_Taiyo-Yuden_NR-50xx_HandSoldering | 2 | WE-74405042047 | x |  | würth
13 | J3 | Pin_Header_Straight_1x03_Pitch2.54mm | 1 | debug_uart | x |  | n
14 | J6 | BNC_Multi | 1 | VIDEO | x | Pomona 6747 | 4
15 | U2 | SOT-353_SC-70-5_Handsoldering | 1 | AP7115 | x |  | 4
16 | MD1 | Socket_SODIMM_DDR1-2_TE_1612618_Debug | 1 | Raspberry Pi CM3 | x |  | n
17 | J8,J9 | MountingHole_2.2mm_M2_Pad | 2 | M2 | n |  | n
18 | J10,J11,J12,J13,J14 | MountingHole_3.2mm_M3_Pad | 5 | M3 | n |  | n
19 | R1 | R_0603_HandSoldering | 1 | 220R | x |  | 3
20 | R6,R7 | R_0603_HandSoldering | 2 | 0R | x |  | 6
21 | R8 | R_0603_HandSoldering | 1 | NF | n | do not assemble | n
22 | R10,R15,R16,R17,R18,R19,R20,R21 | R_0603_HandSoldering | 8 | NC | n | do not assemble | n
23 | R11,R12 | R_0603_HandSoldering | 2 | 100k | x |  | su
24 | Q1,Q2 | SOT-23 | 2 | Q_NMOS_DGS | x | DMG1012UW-7 | 6
25 | R2,R13,R14,R5 | R_0603 | 4 | 100k | x |  | 18
26 | R3 | R_0603 | 1 | 47k | x |  | 3
27 | R4 | R_0603 | 1 | 470R | x |  | 3
28 | C13 | C_0603 | 1 | 1µ | x |  | 3
29 | C14 | C_0603 | 1 | 100n | x |  | würth
30 | C15 | C_0603 | 1 | 4µ7 | x |  | 3
31 | C8,C6 | C_0603 | 2 | 10u | x |  | 18
32 | R9 | R_0603 | 1 | NF | n | do not assemble | n

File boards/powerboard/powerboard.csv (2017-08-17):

Id | Designator | Package | Quantity | Designation | partsbox
1 | FL101,FL102 | WE-SL5 | 2 | 744272471 | x
2 | C101,C104,C108,C503,C505 | C_0805 | 5 | 10µ | x
3 | C102 | C_1206 | 1 | 47µ | x | ! | Ersatz: | 2x C3216X5R1V226M160AC
4 | C105,C107,C302,C304,C305,C306,C308,C309,C310,C311,C312,C315,C504,C701,C702,C801,C802,C803,C901,C902,C1002,C109 | C_0603 | 22 | 100n | x
5 | C106 | C_0805 | 1 | 470n | x
6 | C201 | C_1206 | 1 | 10µ/40V | x |  | 35V
7 | C202 | C_0805 | 1 | 1µ/40V | x |  | 50V
8 | C203,C204 | C_0603 | 2 | 22n | x
9 | C205,C303,C314,C1001 | C_0603 | 4 | 1µ | x
10 | C206 | C_1812_HandSoldering | 1 | 100µ/10V | x
11 | C301,C307,C1003 | C_0603 | 3 | 4µ7 | x
12 | C313 | C_0603 | 1 | 47µ | x | ! | 4u7
13 | C316,C317,C318 | C_0603 | 3 | 100p | x
14 | C501 | C_0603 | 1 | 68n | x
15 | C502 | C_0603 | 1 | 33n | x
16 | C1101,C1102,C1103,C1104,C1105,C1106,C1107,C1108,C1109,C1110,C1111,C1112,C1113,C1114,C1115,C1116 | C_0603 | 16 | 220n | x
17 | D301,D302 | LED_0603 | 2 | LED | x |  | Red & Yellow
18 | D303 | D_SMB_Handsoldering | 1 | Vishay LVB14A 13.2V | x
19 | D304,D305,D306 | D_SMB_Handsoldering | 3 | SMBJ40CA | x
20 | D501 | D_SMB_Handsoldering | 1 | MBRS360BT3G | x
21 | D701,D702 | SOT-23 | 2 | ESD | x |  | PESD1CAN,215
22 | D1001 | D_SMA_Handsoldering | 1 | MBRA140T3 | x
23 | J102 | Pin_Header_Straight_2x20_Pitch2.54mm | 1 | Powerboard <-> Mainboard | x
24 | J105 | MountingHole_3.2mm_M3_Pad_Via | 1 | BOOST | n
25 | J106 | Pin_Header_Straight_1x01_Pitch2.54mm | 1 | Boost24V_EN | x
26 | J107 | MountingHole_3.2mm_M3_Pad_Via | 1 | 24V_1 | n
27 | J108 | MountingHole_3.2mm_M3_Pad_Via | 1 | 24V_2 | n
28 | J109 | MountingHole_3.2mm_M3_Pad_Via | 1 | 24V_3 | n
29 | J110 | MountingHole_3.2mm_M3_Pad_Via | 1 | BAT | n
30 | J111 | MountingHole_3.2mm_M3_Pad_Via | 1 | GND | n
31 | L301,L302,L303 | L_1812 | 3 | 742792515 | x |  | Zusätzlich: WE 74279244
32 | P501 | Pin_Header_Straight_1x02_Pitch2.54mm | 1 | 10k NTC | x |  | Vishay NTCLE100E3223HB0
33 | Q101 | TO-263-3Lead | 1 | SQM40031EL | x
34 | Q102,Q104,Q501 | SOT-23 | 3 | DMN6140L | x
35 | Q502 | SOT-23 | 1 | PMV27UPE | x
36 | Q503 | SOIC-8_3.9x4.9mm_Pitch1.27mm | 1 | IRF7343PBF | x
37 | Q801,Q802,Q803 | SOT-669_LFPAK | 3 | BUK7Y4R8-60E | x
38 | R101,R103,R502,R503,R504,R505,R701,R801,R802,R803,R125,R126,R807,R808,R809 | R_0603 | 15 | 10k | x
39 | R102 | R_0603 | 1 | 20k | x
40 | R104 | R_0603 | 1 | 91k | x
41 | R105 | R_0603 | 1 | 13k | x
42 | R106,R108,R113 | R_0603 | 3 | 15k | x
43 | R107,R109,R110,R111,R501,R601,R602,R603,R114,R607,R608 | R_0603 | 11 | 1k | x
44 | R112,R203,R804,R805,R806,R1002 | R_0603 | 6 | 100k | x
45 | R201 | R_0603 | 1 | 68k1 | x
46 | R202 | R_0603 | 1 | 11k8 | x
47 | R204 | R_0603 | 1 | 5k62 | x
48 | R205 | R_0603 | 1 | 1k07 | x
49 | R301,R302 | R_0603 | 2 | 470 | x
50 | R303 | R_0603 | 1 | 150k | x
51 | R506 | R_0603 | 1 | 50k | x
52 | R507 | R_1812_HandSoldering | 1 | 0.05 | x
53 | R604,R605,R606 | R_0603 | 3 | 3k | x
54 | R1001 | R_0603 | 1 | 140k | x
55 | R1003 | R_0603 | 1 | 4k7 | x
56 | R1004 | R_0603 | 1 | 2R | x
57 | R1101,R1102,R1103,R1104,R1105,R1106,R1107,R1108,R1109,R1110,R1111,R1112,R1113,R1114,R1115,R1116 | R_0603 | 16 | 47k | x
58 | U102 | SOIC-16_3.9x9.9mm_Pitch1.27mm | 1 | DS26LV32AT | x
59 | U201 | 7TO-PMOD | 1 | LMZ14203 | x
60 | U301 | SOT-23 | 1 | LM3480-12 | x
61 | U302 | HSSOP-36 | 1 | DRV8332 | x
62 | U303,U801,U802,U803 | SOIC-8_3.9x4.9mm_Pitch1.27mm | 4 | ACS711 | x | ACS725LLCTR-10AU-T |  | 10A unidirektional
63 | U501 | TSSOP-16-1EP_4.4x5mm_Pitch0.65mm | 1 | LTC4010 | x
64 | U601,U602,U603 | SOP-4 | 3 | PC3H7 | x
65 | U701 | SOIC-14_3.9x8.7mm_Pitch1.27mm | 1 | MAX13432EESD | x
66 | U901 | TSSOP-20_4.4x6.5mm_Pitch0.65mm | 1 | AD7928 | x
67 | U902 | SOT-23 | 1 | REF3025 | x
68 | U1001 | MSOP-10-1EP_3x3mm_Pitch0.5mm | 1 | LT3592 | x
69 | U1101,U1102 | TSSOP-14_4.4x5mm_Pitch0.65mm | 2 | LMV324 | x
70 | C103 | C_0805 | 1 | 1µ | x
71 | L101 | L_Coilcraft_1583_Handsoldering | 1 | Coilcraft MSS1583-474 | x
72 | L501 | L_Coilcraft_XAL60xx_Handsoldering | 1 | Coilcraft XAL6060-822 | x
73 | L1001 | L_Coilcraft_XAL40xx_Handsoldering | 1 | Coilcraft XAL4040-103 | x
74 | U101 | SOT-223 | 1 | LM1117-3.3 | x
75 | J112,J113,J114,J115,J116,J117,J118 | MountingHole_3.2mm_M3_Pad | 7 | M3 | n
76 | R115,R116,R117,R118,R119,R120,R121 | R_0603 | 7 | NC | n
77 | FL701,FL702 | WE-SL2 | 2 | CMC | x | WE 744228
78 | C319,C804,C805,C806 | C_0603 | 4 | 1n | x
79 | R122,R123,R124 | R_0603 | 3 | 0 | x
80 | J101 | DB15MD | 1 | RXSM experiment connector
81 | J103 | DB9FD | 1 | Cameraboard
82 | J104 | DB15FD | 1 | BLDC Motor
83 | J810 | MountingHole_3.2mm_M3_Pad_Via | 1 | HP1 | n
84 | J811 | MountingHole_3.2mm_M3_Pad_Via | 1 | HP2 | n
85 | J812 | MountingHole_3.2mm_M3_Pad_Via | 1 | HP3 | n
86 | C110,C111,C112,C113,C114,C115,C116,C117 | C_0603 | 8 | 10n | x
87 | D101 | LED_0603 | 1 | RX-PW | x | Green
88 | D102 | LED_0603 | 1 | RX-CHG | x | Red
89 | D103 | LED_0603 | 1 | BAT | x | Blue
90 | D801 | LED_0603 | 1 | HP1 | x | Yellow
91 | D802 | LED_0603 | 1 | HP2 | x | Yellow
92 | D803 | LED_0603 | 1 | HP3 | x | Yellow
93 | R127 | R_0603 | 1 | 4k | x
94 | TP101 | Measurement_Point_Round-SMD-Pad_Small | 1 | 28V | n
95 | TP102 | Measurement_Point_Round-SMD-Pad_Small | 1 | CHG | n
96 | TP103 | Measurement_Point_Round-SMD-Pad_Small | 1 | +5V | n
97 | TP104 | Measurement_Point_Round-SMD-Pad_Small | 1 | +3V3 | n
98 | TP105,TP106 | Measurement_Point_Round-SMD-Pad_Small | 2 | GND | n
99 | TP107 | Measurement_Point_Round-SMD-Pad_Small | 1 | HP3C | n
100 | TP108 | Measurement_Point_Round-TH_Small | 1 | GND | n
101 | TP109 | Measurement_Point_Round-SMD-Pad_Small | 1 | HP2C | n
102 | TP110 | Measurement_Point_Round-SMD-Pad_Small | 1 | HP1C | n
103 | TP111 | Measurement_Point_Round-SMD-Pad_Small | 1 | V_MOTOR | n
104 | TP112 | Measurement_Point_Round-SMD-Pad_Small | 1 | MOTORC | n

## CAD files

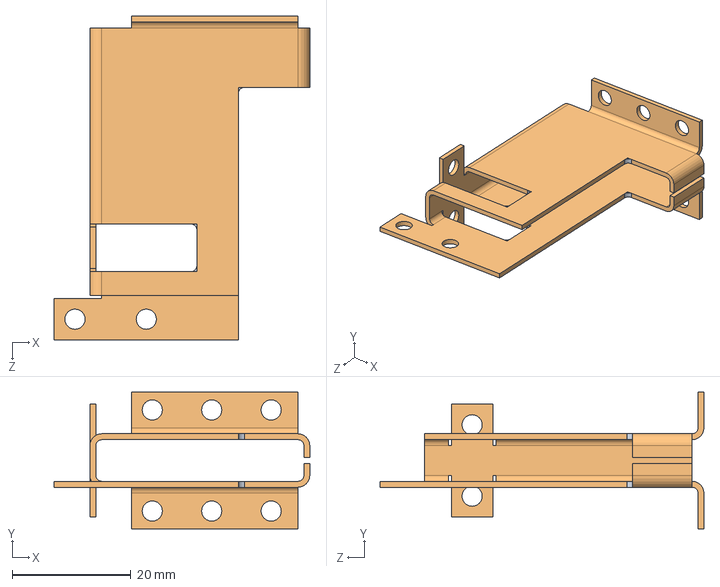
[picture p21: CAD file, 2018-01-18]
mech_cad/Blech-Abwicklung/HPPM_OS_Cablerun_Vergleich.SLDASM
43.0 x 23.0 x 54.5 mm
HPPM_OS_Cablerun_Blech
HPPM_OS_Cablerun_NEU

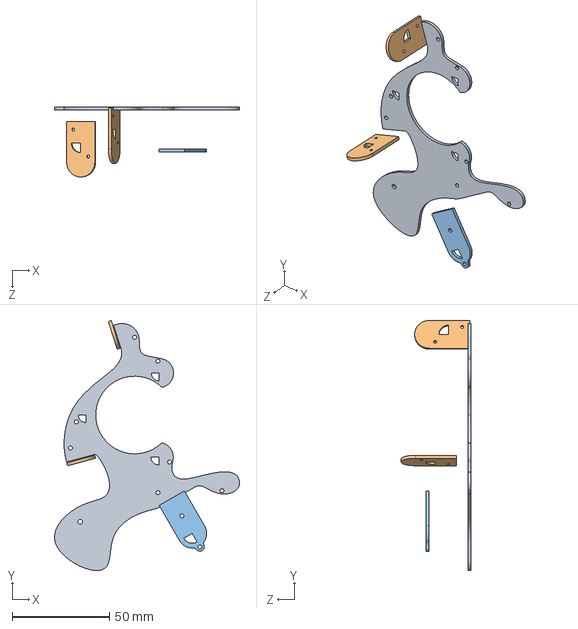
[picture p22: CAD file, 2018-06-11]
mech_cad/hppm-rotation-encoder/Cupola-Cable-Boards-Assembly.STEP
95.3 x 128.7 x 36.0 mm

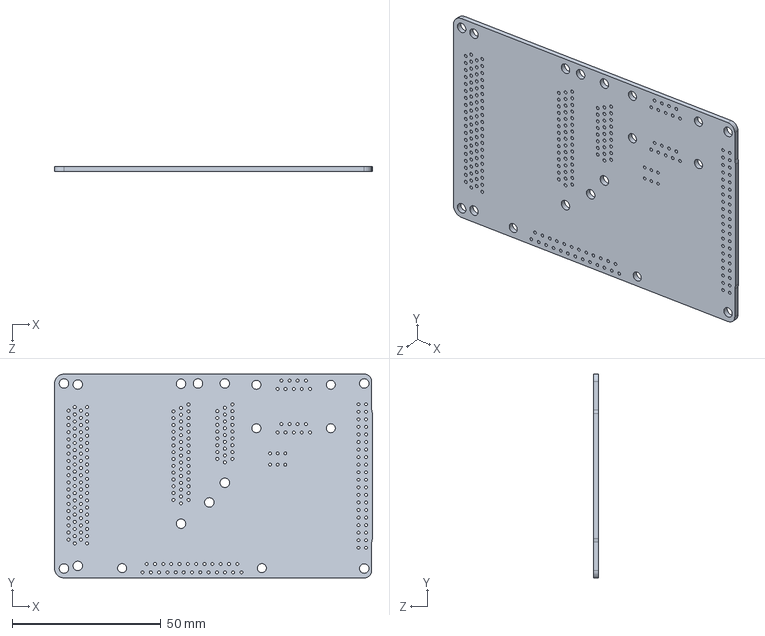
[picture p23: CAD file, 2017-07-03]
mech_cad/mainboard-and-powerboard/assembly/mainboard.SLDPRT
106.9 x 68.6 x 1.60 mm

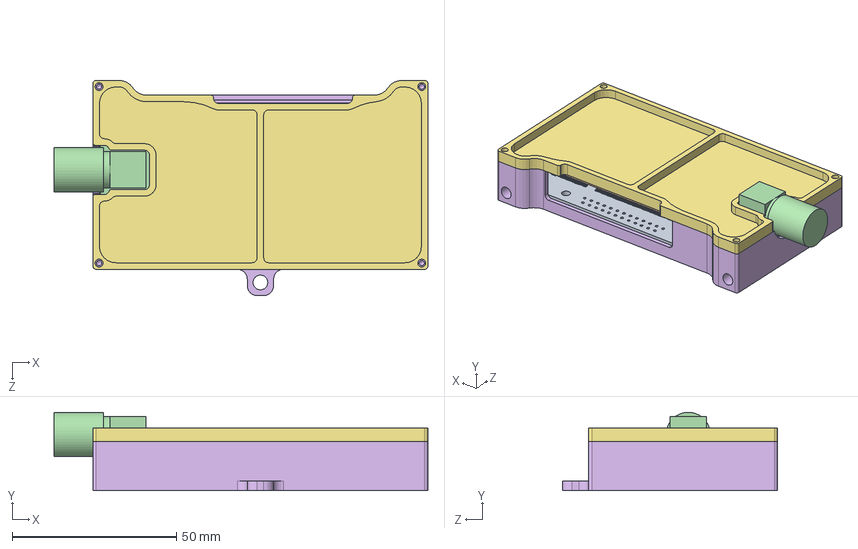
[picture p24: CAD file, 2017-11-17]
mech_cad/pi-board/assembly/Pi-Board-Assembled.SLDASM
113.8 x 23.8 x 65.5 mm
pi-board
DIMM-Socket_TE-1612618
Schraube_M2x12 x 2
BNC-Angled_Pomona-6748
computeModule
Pi-Case
Pi-Case-cover

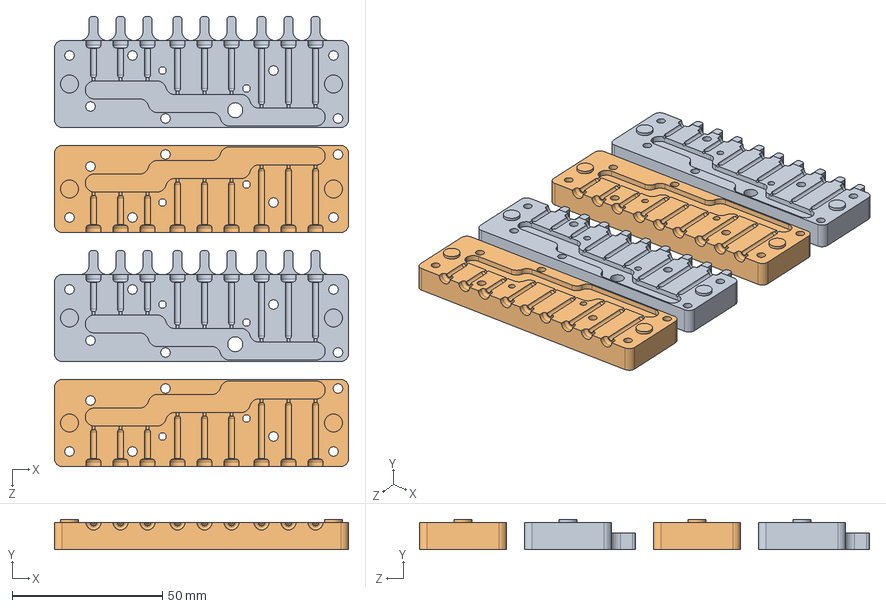
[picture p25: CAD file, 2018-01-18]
mech_cad/Pt100-Gussform/Pt100-Gussformen.SLDASM
98.0 x 10.0 x 150.0 mm
Pt100-Gussform-SchaleA x 2
SpiegelnPt100-Gussform-SchaleA x 2

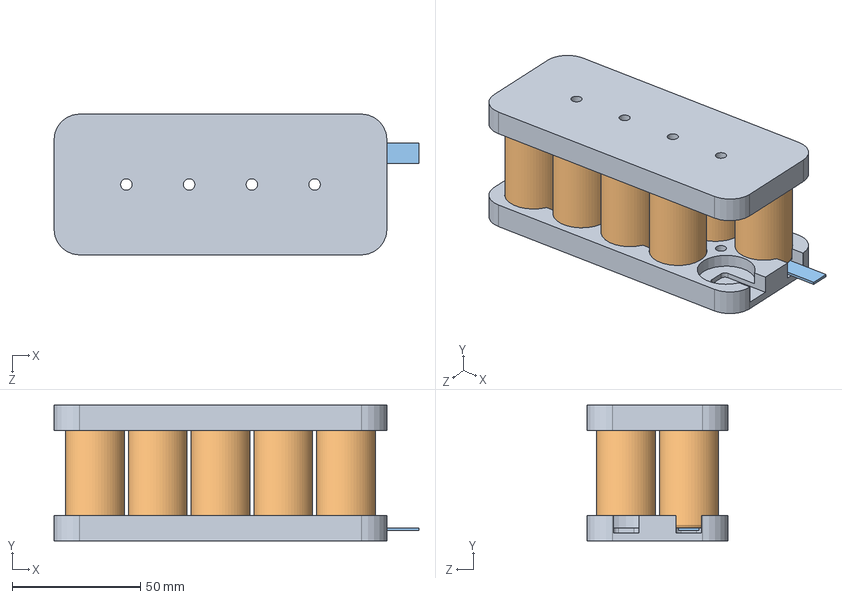
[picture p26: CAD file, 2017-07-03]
mech_cad/battery-pack/Battery_Pack_9Zellen.SLDASM
142.5 x 53.0 x 55.0 mm
Zellenhalterung x 2
BK300SCP_Zelle x 9
Zellenverbinder x 10

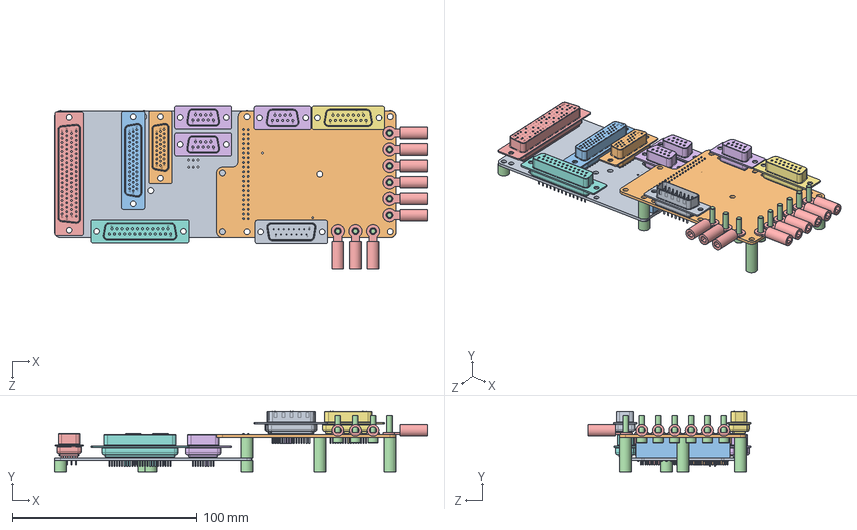
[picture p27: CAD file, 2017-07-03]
mech_cad/mainboard-and-powerboard/assembly/MainboardAndPowerboard.SLDASM
201.9 x 32.8 x 88.4 mm
mainboard
powerboard_rev4
Platinenverbinder_2x20
Distanzhalter x 11
b-DIN EN ISO 4762-M3x12 x 9
Cable-Lug_TE-2-34852-1 x 9

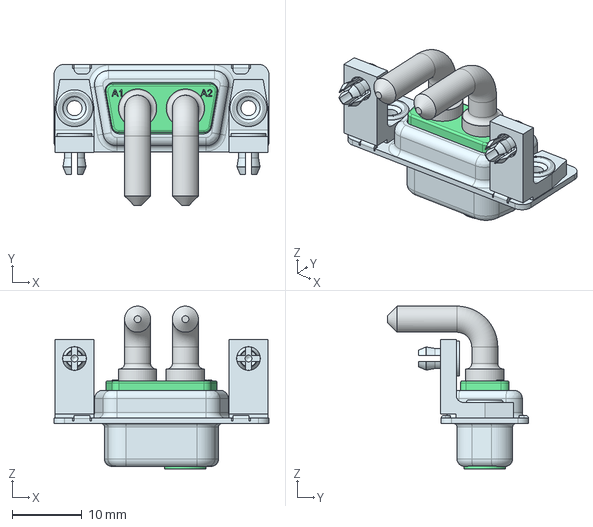
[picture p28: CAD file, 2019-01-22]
boards/batterie-connector/302W2CSXX60N40X.stp
30.9 x 20.3 x 23.4 mm

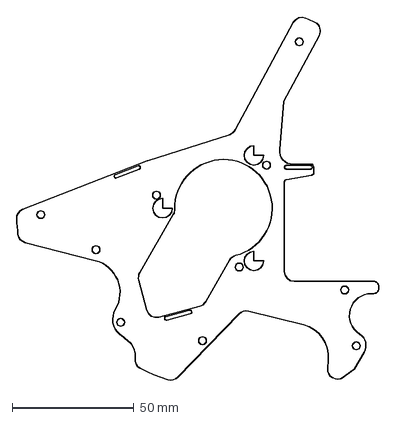
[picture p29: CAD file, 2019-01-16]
boards/cupola-cable-board/Cupola_Bulkhead_Board_Outline.dxf
148.6 x 149.7 mm

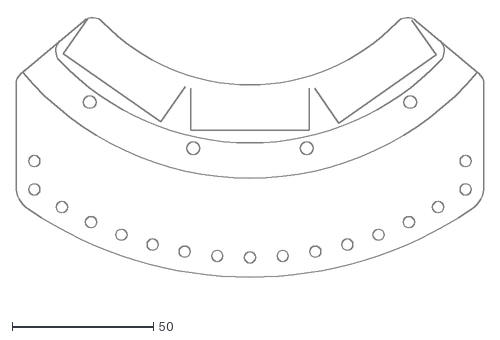
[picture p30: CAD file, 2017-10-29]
boards/CupolaFeedthrough/Cupola_Bottom_PCB.dxf
165.5 x 100.3

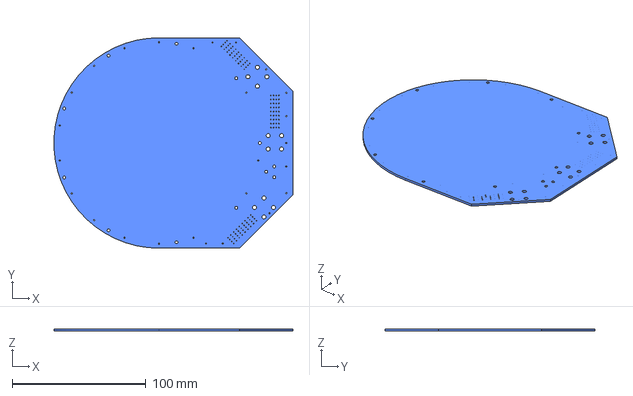
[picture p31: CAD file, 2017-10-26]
boards/iscaBottom/iscaBottom.step
178.4 x 157.0 x 1.60 mm

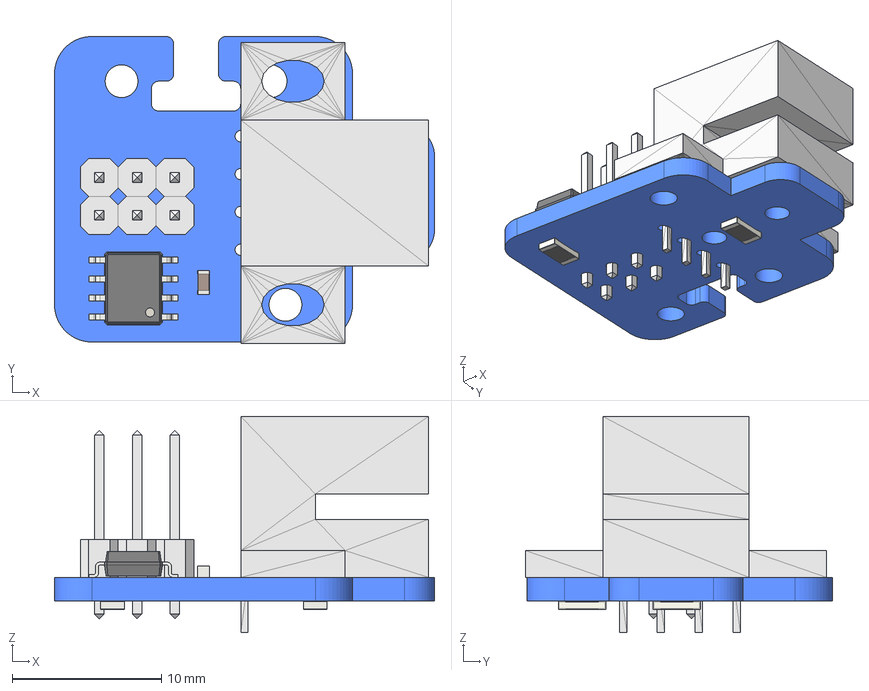
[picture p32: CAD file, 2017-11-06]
boards/optical-distance/optical-distance.step
25.5 x 20.6 x 14.5 mm
Pcb
HEDS_973X_X50001_(Solid)_
SOIC-8_3.9x4.9mm_Pitch1.27mm_
C_0603_
R_1206_
R_1206_001

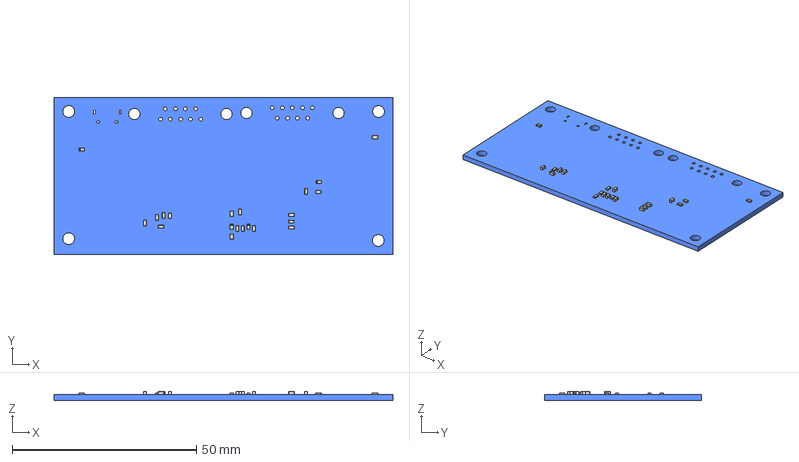
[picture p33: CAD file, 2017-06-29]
boards/pi-board/pi_board.FCStd
92.0 x 42.5 x 2.38 mm
Pcb
R_0603_
C_0603_
C_0603_001
C_0603_002
C_0603_003
C_0603_004
C_0603_005
C_0603_006
C_0603_007
C_0603_008
C_0603_009
C_0603_010
C_0603_011
R_0603_001
R_0603_002
R_0603_003
R_0603_004
R_0603_005
R_0603_006
R_0603_007
R_0603_008

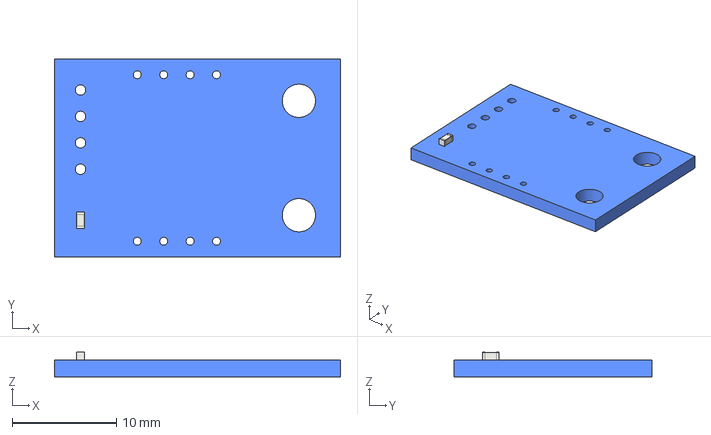
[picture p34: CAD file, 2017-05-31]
boards/pressure-sensor-hcla/pressure_sensor_hcla.FCStd
27.5 x 19.0 x 2.38 mm
Pcb
C_0603_

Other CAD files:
mech_cad/mainboard-and-powerboard/mainboard.step
boards/pressure-sensor/pressure_sensor.FCStd
mech_cad/ams5915v2/ams5915v2.step
mech_cad/battery-pack/BK300SCP_Zelle.SLDPRT
mech_cad/Blech-Abwicklung/HPPM_OS_Arm_Extension.SLDPRT
mech_cad/Blech-Abwicklung/HPPM_OS_Arm_Extension.stp
mech_cad/Blech-Abwicklung/HPPM_OS_Arm_Extension_Blech.DXF
mech_cad/Blech-Abwicklung/HPPM_OS_Arm_Extension_Blech.SLDPRT
mech_cad/Blech-Abwicklung/HPPM_OS_Cablerun.SLDPRT
mech_cad/Blech-Abwicklung/HPPM_OS_Cablerun.stp
mech_cad/Blech-Abwicklung/HPPM_OS_Cablerun_Blech.DXF
mech_cad/Blech-Abwicklung/HPPM_OS_Cablerun_Blech.SLDPRT
mech_cad/Blech-Abwicklung/HPPM_OS_Cablerun_Blech.STEP
mech_cad/Blech-Abwicklung/HPPM_OS_Cablerun_Blech_Abwicklung.DXF
mech_cad/Blech-Abwicklung/HPPM_OS_Cablerun_Blech_Abwicklung_Weniger_Loecher.DXF
mech_cad/Blech-Abwicklung/HPPM_OS_Cablerun_NEU.SLDPRT
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

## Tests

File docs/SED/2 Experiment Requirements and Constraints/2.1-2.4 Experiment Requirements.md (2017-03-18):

## 2.1 Functional
    Electronics
    F. 9: The experiment shall measure the temperature distribution in each block of ice.
    F.10: The pressure above each ice block shall be measured.
    F.15: The penetration depth of the heat probes shall be measured.
    F.12: All acquired data shall be stored redundantly on reliable data storage devices.
    F.16: The power for the heat probes shall be provided by NiMH batteries.
    F.17: The power for the other electric components shall be provided by RXSM.

    Software
    F.11: All acquired data except for the camera data shall be sent to the ground station via RXSM downlink.
    F.12: The software shall be reliable, under all circumstances.

## 2.2 Performance
    Electronics
    P.21: The temperature sensors shall measure in a range of -80 to 0 °C.
    P.16: The temperature sensors shall measure with an accuracy of 0.5 °C or better.
    P.17: The temperature data shall be acquired with a sample rate of 1 Hz or higher.

    P.18: The pressure sensors shall measure in a range of 0 to 5 mbar.
    P.19: The pressure sensors shall measure with an accuracy of 1 mbar or better.
    P.22: The pressure data shall be acquired with a sample rate of 20 Hz or higher.

    P.23: The penetration depth shall be measured with an accuracy of 0.5 mm or lower.
    P.24: The force sensors shall measure in a range of 0 to 40 N.
    P.25: The force sensors shall measure with an accuracy of 0.039 N or better.
    P.26: The force data shall be acquired with a sample rate of 2 Hz or higher.

    P.27: The batteries shall provide 180 W of power for at least 3 min of experiment time.
    P.20: The total power consumption shall be below 200 W.

    P.28: There shall be enough storage for 30 min of data acquisition.
    P.29: All data shall be stored with a redundancy factor of 2 or more.

    Software

## 2.3 Design
    Electronics
    D.18: The temperature distribution in each ice block shall be measured by a 3x3 temperature sensor matrix.
    D.17: The pressure shall be measured by differential pressure sensors.
    D.19: The penetration depth shall be measured indirecly using force sensors on each spring-loaded heat probe.
    D.20: There shall be no electrical connection of electronic components to the rocket structure.
    D.21: No electronics shall be enabled during radio silence.
    D.22: The power consumption of all electronics combined (except for the heat probes) shall be below the 30 W supplied by the RXSM.
    D.23: The electronic components must endure the thermal environment during the launch and flight.
    D.24: The electronic components must endure 20 g loads in all axis.
    D.25: The electronic must be able to cope with vacuum (lack of thermal convection).

    Software
    D.16: The data rate sent to the RXSM for downlink shall be below 20 kbit/s.

## 2.4 Operational
    Electronics
    O. 4: The battery’s temperature shall not exceed the operational window.

    Software
    O. 5: The heat probes shall be turned off in case of over heating.
    O. 6: The experiment shall accept a request for radio silence at any time while on the launch pad.
    O. 7: The experiment shall be able to conduct measurements autonomously in case connection with the ground segment is lost.
    O. 8: The experiment shall be able to enter a secure mode after landing (sensitive equipment shall be disabled, moving parts locked).

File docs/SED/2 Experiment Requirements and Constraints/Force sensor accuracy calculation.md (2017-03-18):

### From the science team requirements:
> 2.2.1.2 Penetration depth
> P.7: The penetration depth shall be measured with an accuracy of ±0.5 mm or lower.

∆s = 0.0005 m

### From the structure guys HPPM documentation:
> Federweg: 45-50 mm, Höchstkraft: 38,6 N

k = F / s = 38.6 N / 0.05 m = 772 N/m

Assumption: There might be a 10 times weaker spring

k /= 10 = 77.2 N/m

### Estimating the required force sensing accuracy

F = k * s
∆F = k * ∆s = 77.2 N/m * 0.0005 m = 0,0386 N

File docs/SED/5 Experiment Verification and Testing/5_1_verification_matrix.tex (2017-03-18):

\documentclass[11pt]{scrartcl} 
\usepackage{textcomp}
\usepackage{longtable}

\begin{document}
 \section{Verification Matrix}
 
 Verification methods: \textbf{T}est, \textbf{I}nspection, \textbf{A}nalysis / Similarity, \textbf{R}eview of design
 
 \begin{center}
	\begin{longtable}{| p{.06\textwidth} | p{.50\textwidth} | p{.14\textwidth} | p{.16\textwidth} | p{.14\textwidth} |}
		\hline
		ID & Requirement text & Verification & Test number & Status \\
		\hline
		F.9 & The experiment shall measure the temperature distribution in each block of ice. & I & - & tbd \\
		F.10 & The pressure above each ice block shall be measured. & I & - & tbd \\
		F.15 & The penetration depth of the heat probes shall be measured. & I & - & tbd \\
		F.12 & All acquired data shall be stored reliably on reliable data storage devices. & A, R & - & tbd \\
		F.16 & The power for the heat probes shall be provided by NiMH batteries. & R & - & tbd \\
		F.17 & The power for the other electric components shall be provided by RXSM. & R & - & tbd \\
		F.11 & All acquired data except for the camera data shall be sent to the ground station via RXSM downlink. & I & - & tbd \\
		F.12 & The software shall be reliable, under all circumstances. & A, T & Test 3 & tbd \\
		\hline
		P.21 & The temperature sensors shall measure in a range of -80 to 0 \textdegree C. & R & - & tbd \\
		P.16 & The temperature sensors shall measure with an accuracy of 0.5 \textdegree C or better. & R, T & Test 1 & tbd \\
		P.17 & The temperature data shall be acquired with a sample rate of 1 Hz or higher. & R & - & tbd \\
		P.18 & The pressure sensors shall measure in a range of 0 to 5 mbar. & R & - & tbd \\
		P.19 & The pressure sensors shall measure with an accuracy of 1 mbar or better. & R, T & Test 1 & tbd \\
		P.22 & The pressure data shall be acquired with a sample rate of 20 Hz or higher\textsl{}. & R & - & tbd \\
		P.23 & The penetration depth shall be measured with an accuracy of 0.5 mm or lower. & T & Test 1 & tbd \\
		P.24 & The force sensors shall measure in a range of 0 to 40 N. & R & - & tbd \\
		P.25 & The force sensors shall measure with an accuracy of 0.039 N or better. & R, T & Test 1 & tbd \\
		P.26 & The force data shall be acquired with a sample rate of 2 Hz or higher. & R & - & tbd \\
		P.27 & The batteries shall provide 180 W of power for at least 3 min of experiment time. & A & - & tbd \\
		P.20 & The total power consumption shall be below 200 W. & A & - & tbd \\
		P.28 & There shall be enough storage for 30 min of data acquisition. & A & - & tbd \\
		P.29 & All data shall be stored with a redundancy factor of 2 or more. & R & - & tbd \\
		\hline
		D.18 & The temperature distribution in each ice block shall be measured by a 3x3 temperature sensor matrix. & I & - & tbd \\
		D.17 & The pressure shall be measured by differential pressure sensors. & I & - & tbd \\
		D.19 & The penetration depth shall be measured indirecly using force sensors on each spring-loaded heat probe. & I & - & tbd \\
		D.20 & There shall be no electrical connection of electronic components to the rocket structure. & R & - & tbd \\
		D.21 & No electronics shall be enabled during radio silence. & R & - & tbd \\
		D.22 & The power consumption of all electronics combined (except for the heat probes) shall be below the 30 W supplied by the RXSM. & R & - & tbd \\
		D.23 & The electronic components must endure the thermal environment during the launch and flight. & A, T & Test 2 & tbd \\
		D.24 & The electronic components must endure 20 g loads in all axis. & A, T & Test 2 & tbd \\
		D.25 & The electronic must be able to cope with vacuum (lack of thermal convection). & A, T & Test 2 & tbd \\
		D.16 & The data rate sent to the RXSM for downlink shall be below 20 kbit/s. & A & - & tbd \\
		
		\hline
		O.4 & The battery’s temperature shall not exceed the operational window. & A & - & tbd \\
		O.5 & The heat probes shall be turned off in case of over heating. & R & - & tbd \\
		O.6 & The experiment shall accept a request for radio silence at any time while on the launch pad. & R & - & tbd \\
		O.7 & The experiment shall be able to conduct measurements autonomously in case connection with the ground segment is lost. & R & - & tbd \\
		O.8 & The experiment shall be able to enter a secure mode after landing (sensitive equipment shall be disabled, moving parts locked). & R & - & tbd \\
		\hline
	\end{longtable}
\end{center}
 
\end{document}

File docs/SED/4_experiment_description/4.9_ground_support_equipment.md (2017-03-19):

## 4.9. Ground support equipment
We use a Laptop with our groundstation software to visualize and store the experiment data, an uplink is only needed for testing.
The laptop is connected to SCIENCE-NET via TCP an shall be able to use RS-232 as fallback.
For further information about our groundstation software see section 4.8 software design.

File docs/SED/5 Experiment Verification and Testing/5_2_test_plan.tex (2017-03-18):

\documentclass[11pt]{scrartcl} 
\usepackage{textcomp}
\usepackage{longtable}

\begin{document}
 \section{Verification Matrix}
 \begin{center}
	\begin{longtable}{| p{.25\textwidth} | p{.75\textwidth} |}
		\hline
		
		Test number & Test 1 \\
		Test type & Precision \\
		Test facility & FH Aachen \\
		Tested item & All sensors \\
		Test level/procedure and duration & Verify if required accuracy can be reached \\
		Test campaign duration & 1 week \\
		Test campaign date &  \\
		Test completed & No \\
		
		\hline\hline
		
		Test number & Test 2 \\
		Test type & Thermal, vacuum, vibration \\
		Test facility & FH Aachen \\
		Tested item & All electronics \\
		Test level/procedure and duration & Test if electronics can withstand the thermal and mechanical loads they will be subjected to in the rocket \\
		Test campaign duration & 1 week \\
		Test campaign date &  \\
		Test completed & No \\
		
		\hline\hline
		
		Test number & Test 3 \\
		Test type & RXSM electrical interface simulation \\
		Test facility & FH Aachen \\
		Tested item & All electronics \\
		Test level/procedure and duration & Simulate communication with the RXSM through a RXSM Simulator: Uplink/downlink and timeline events (LO, SOE) \\
		Test campaign duration & 1 week \\
		Test campaign date &  \\
		Test completed & No \\
		
		\hline
		
	\end{longtable}
\end{center}
 
\end{document}

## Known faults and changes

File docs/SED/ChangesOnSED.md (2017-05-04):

# Changes on SED
```
4.3 	Strain Measurement Devices Omega LCMKD
4.7 	The experiment requires 3 heating probes with a nominal power consumptionof 35W + 70W + 70W
		The power is delivered by 8 battery  cells  (see  data  sheet)
```

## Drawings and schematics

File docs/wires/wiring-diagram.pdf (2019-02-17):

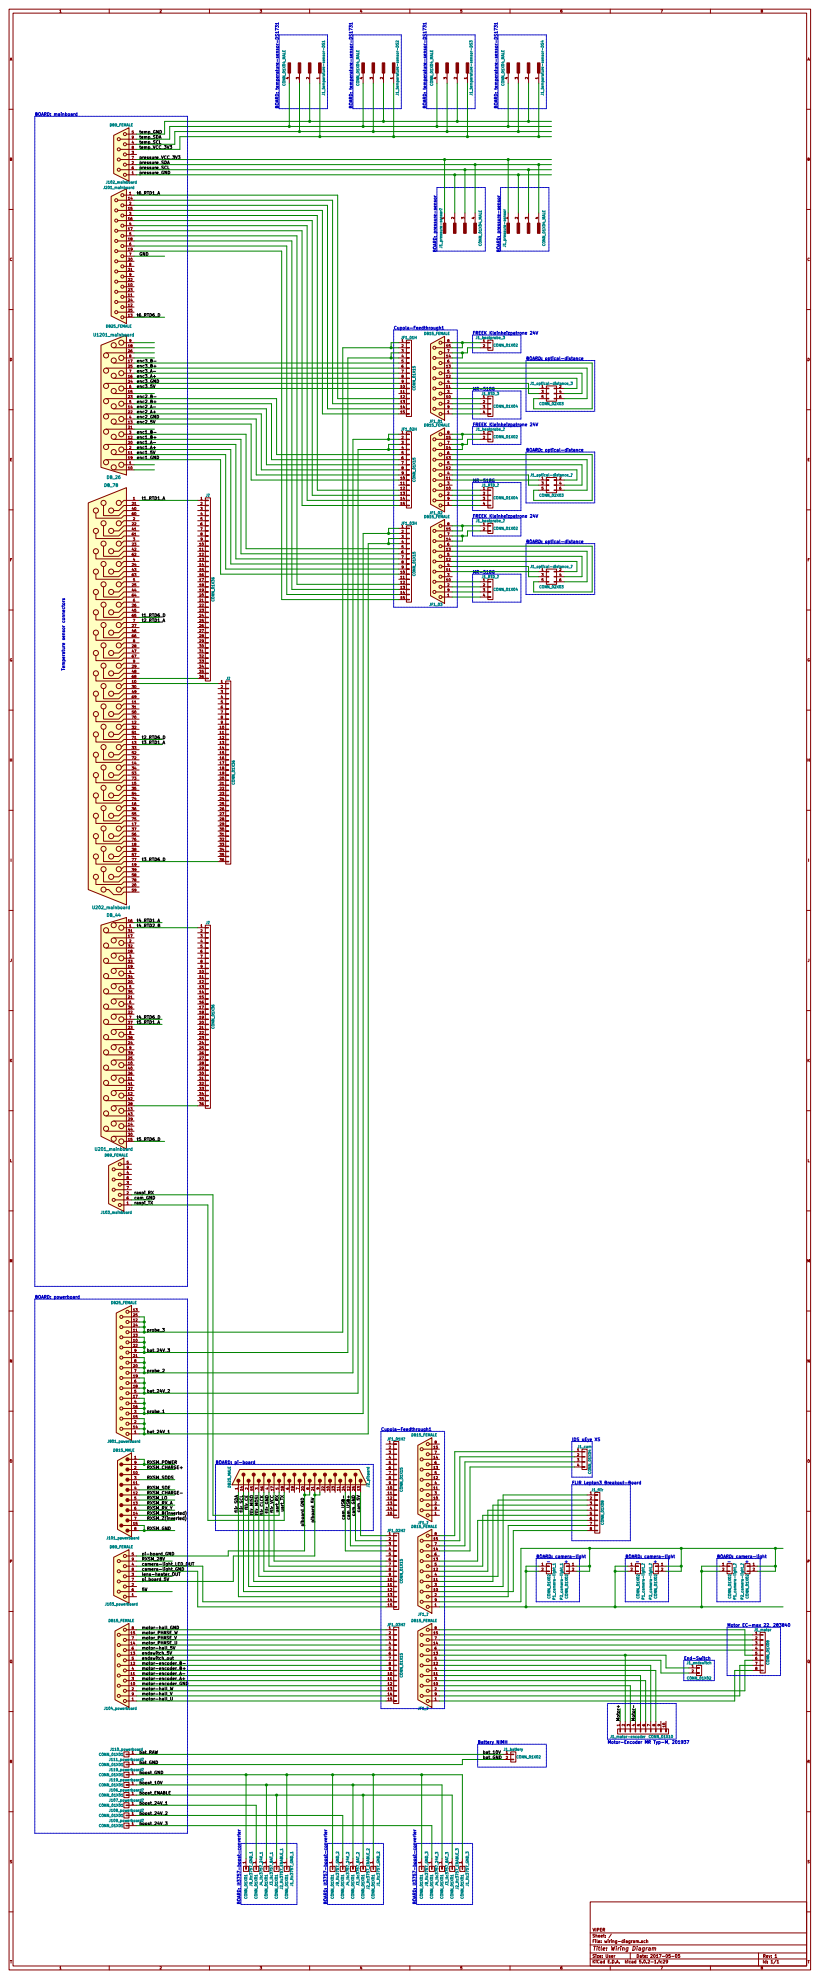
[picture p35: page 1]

1 J1_temperature-sensor-DS1 CONN_01X04_MALE BOARD: temperature-sensor-DS1731

1 J1_temperature-sensor-DS2 CONN_01X04_MALE BOARD: temperature-sensor-DS1731 4

1 J1_temperature-sensor-DS3 CONN_01X04_MALE BOARD: temperature-sensor-DS1731 4

1 J1_temperature-sensor-DS4 CONN_01X04_MALE BOARD: temperature-sensor-DS1731 4

Motor-Encoder MR Typ-M, 201937

File: wiring-diagram.sch Sheet: / VIPER

Id: 1/1 Title: Wiring Diagram

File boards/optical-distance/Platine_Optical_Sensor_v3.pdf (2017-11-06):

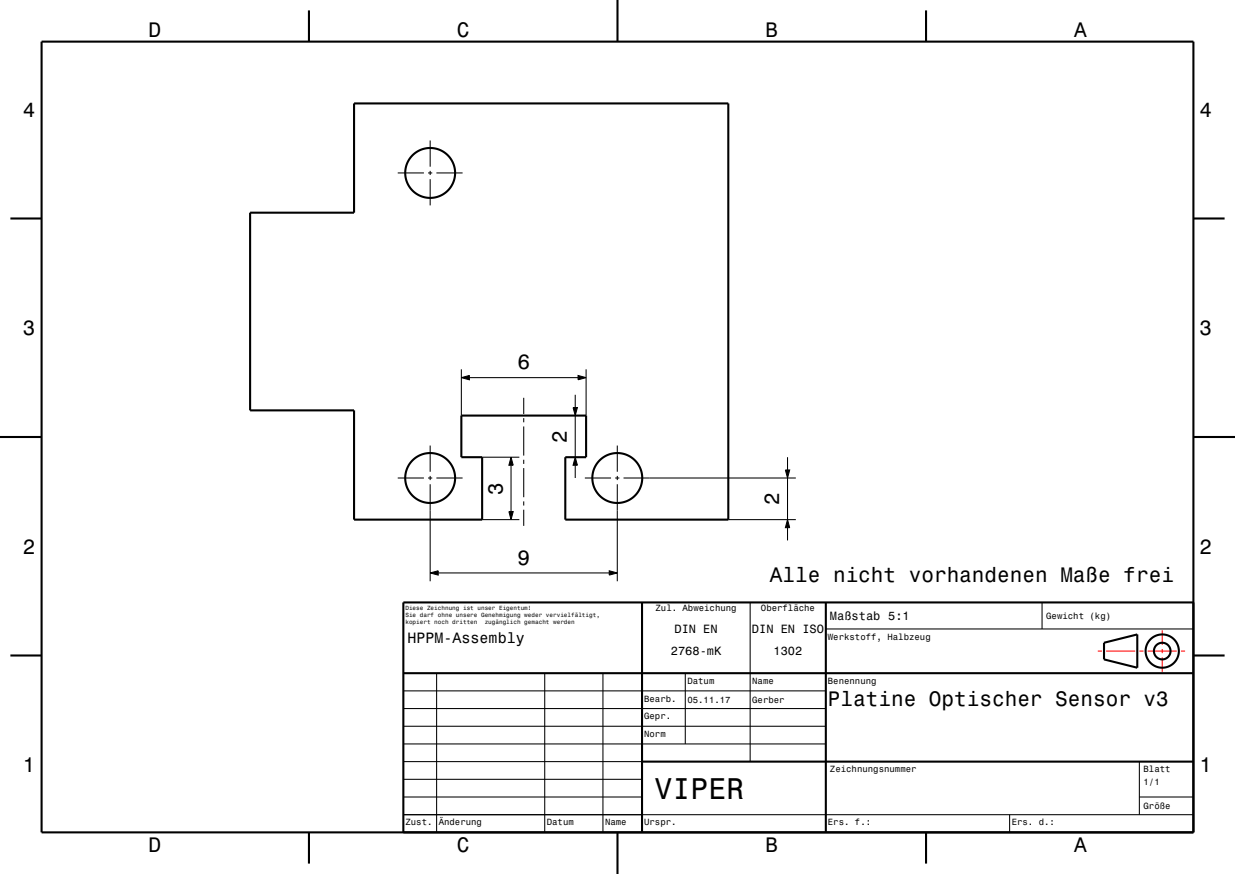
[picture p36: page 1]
kopiert noch dritten zugänglich gemacht werden; Maßstab; Gewicht (kg); Zul. Abweichung; Oberfläche; Werkstoff, Halbzeug; Zust.; Änderung; Datum; Name; Urspr.; Ers. f.:; Ers. d.:; HPPM-Assembly; DIN EN

Alle nicht vorhandenen Maße frei

Diese Zeichnung ist unser Eigentum!
Sie darf ohne unsere Genehmigung weder vervielfältigt,

DIN EN ISO

Datum | Name | Benennung Platine Optischer Sensor v3

Bearb. | 05.11.17 | Gerber

Gepr.
Norm

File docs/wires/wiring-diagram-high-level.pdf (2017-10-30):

# VIPER-HIGH-LEVEL-CABLE-DIAGRAM

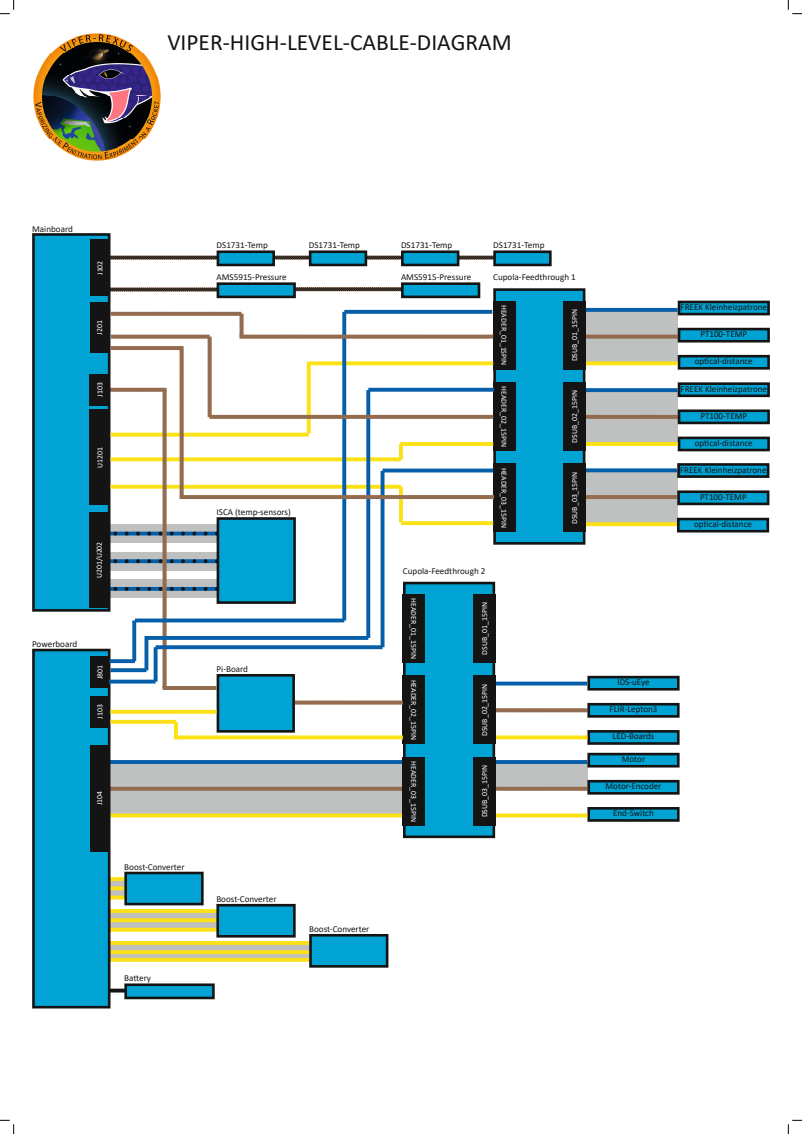
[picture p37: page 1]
DS1731-Temp; AMS5915-Pressure; Mainboard; Pi-Board; Powerboard; FREEK Kleinheizpatrone; Ba ery; Boost-Converter; Cupola-Feedthrough 1 HEADER_01_15PIN; PT100-TEMP; DSUB_01_15PIN; DSUB_02_15PIN; DSUB_03_15PIN; HEADER_02_15PIN HEADER_03_15PIN; Motor; Cupola-Feedthrough 2 HEADER_01_15PIN; Motor-Encoder; End-Switch; IDS-uEye; FLIR-Lepton3; LED-Boards; DSUB_02_15PIN DSUB_03_15PIN

op cal-distance

ISCA (temp-sensors)

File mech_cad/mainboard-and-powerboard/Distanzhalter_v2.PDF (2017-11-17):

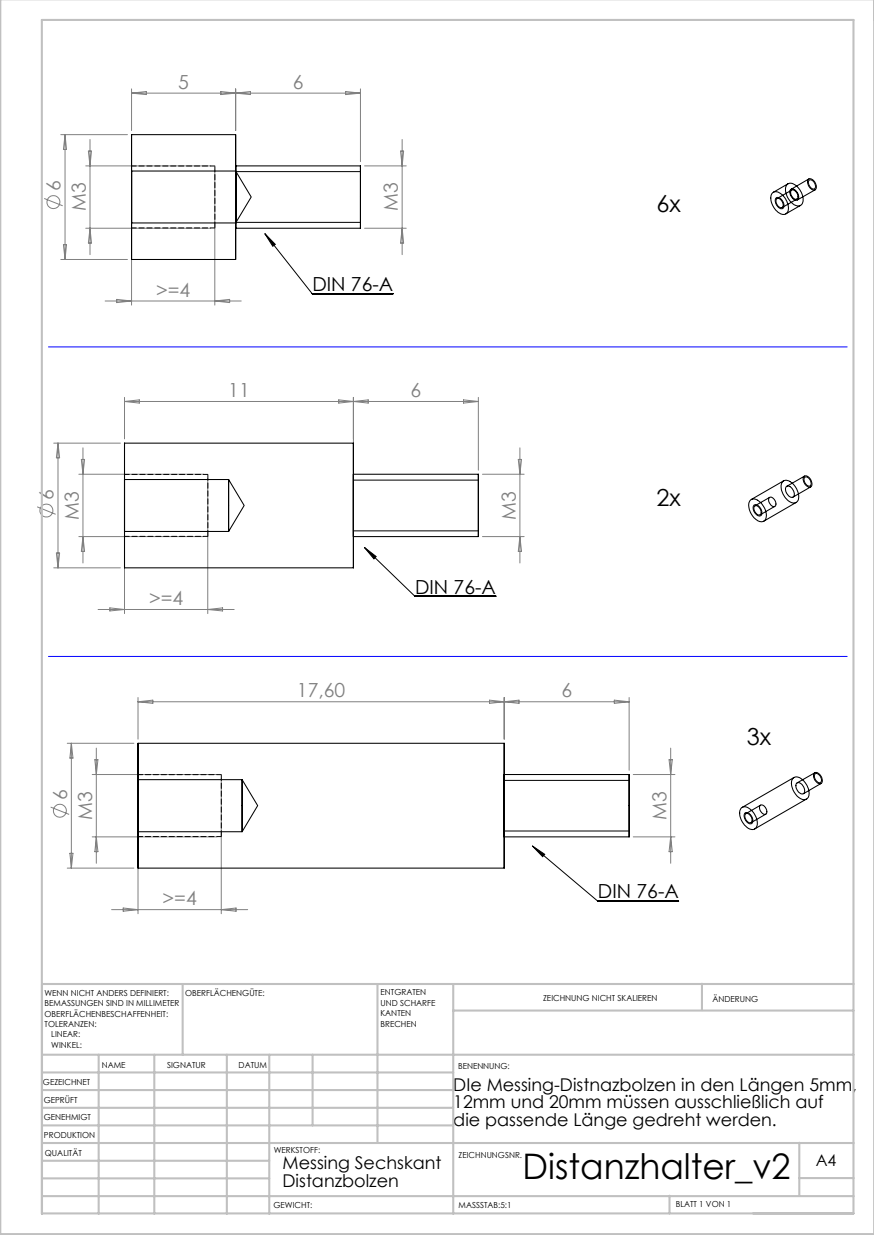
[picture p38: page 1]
DIN 76-A; MASSSTAB:5:1; BLATT 1 VON 1; ZEICHNUNG NICHT SKALIEREN; ÄNDERUNG; UND SCHARFE; WENN NICHT ANDERS DEFINIERT:; OBERFLÄCHENGÜTE:

5 >=4 | 6 DIN 76-A

>=4 | 11 6 DIN 76-A

BEMASSUNGEN SIND IN MILLIMETER
OBERFLÄCHENBESCHAFFENHEIT:
TOLERANZEN:
LINEAR:
WINKEL:

NAME | SIGNATUR | DATUM | | | | BENENNUNG: 12mm und 20mm müssen ausschließlich auf die passende Länge gedreht werden.

DIe Messing-Distnazbolzen in den Längen 5mm,

GEZEICHNET
GEPRÜFT
GENEHMIGT
PRODUKTION
QUALITÄT | | | | WERKSTOFF: Messing Sechskant Distanzbolzen | Distanzhalter_v2 GEWICHT: ZEICHNUNGSNR. | A4

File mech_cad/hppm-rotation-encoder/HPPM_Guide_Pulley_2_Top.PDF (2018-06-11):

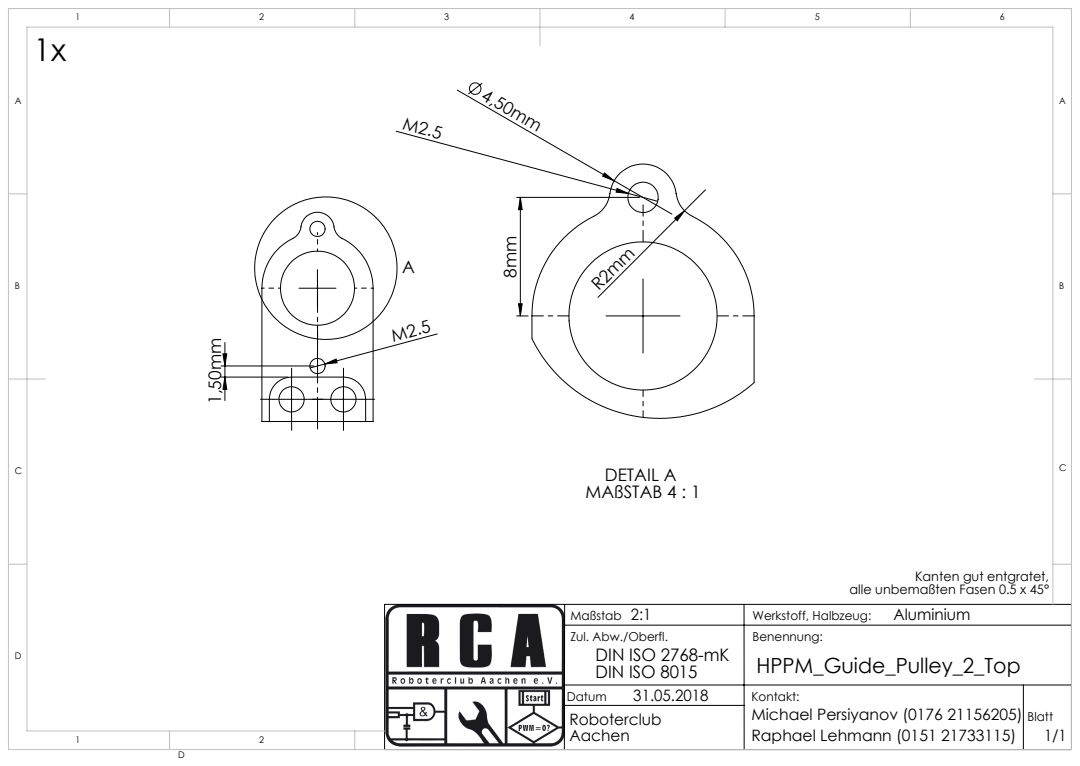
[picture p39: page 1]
DETAIL A MAßSTAB 4 : 1

Kanten gut entgratet,

alle unbemaßten Fasen 0.5 x 45°

Maßstab 2:1 | Werkstoff, Halbzeug: Aluminium
Zul. Abw./Oberfl. DIN ISO 2768-mK DIN ISO 8015 | Benennung: HPPM_Guide_Pulley_2_Top

31.05.2018 Datum | Kontakt: Michael Persiyanov (0176 21156205) Raphael Lehmann (0151 21733115) | Blatt 1/1

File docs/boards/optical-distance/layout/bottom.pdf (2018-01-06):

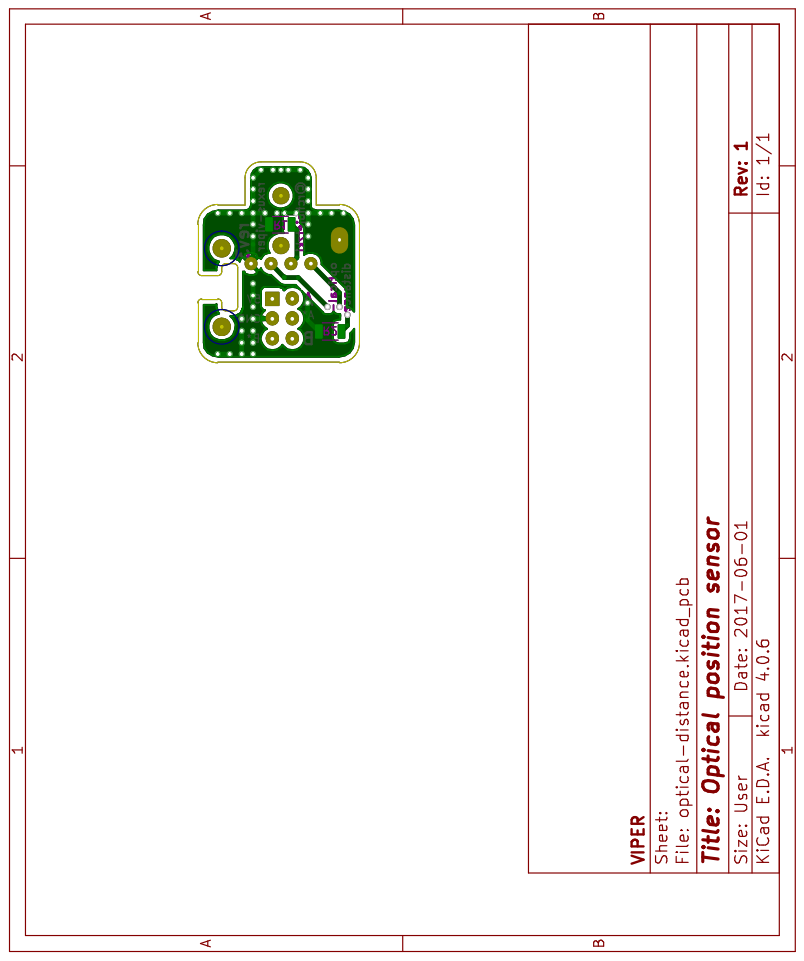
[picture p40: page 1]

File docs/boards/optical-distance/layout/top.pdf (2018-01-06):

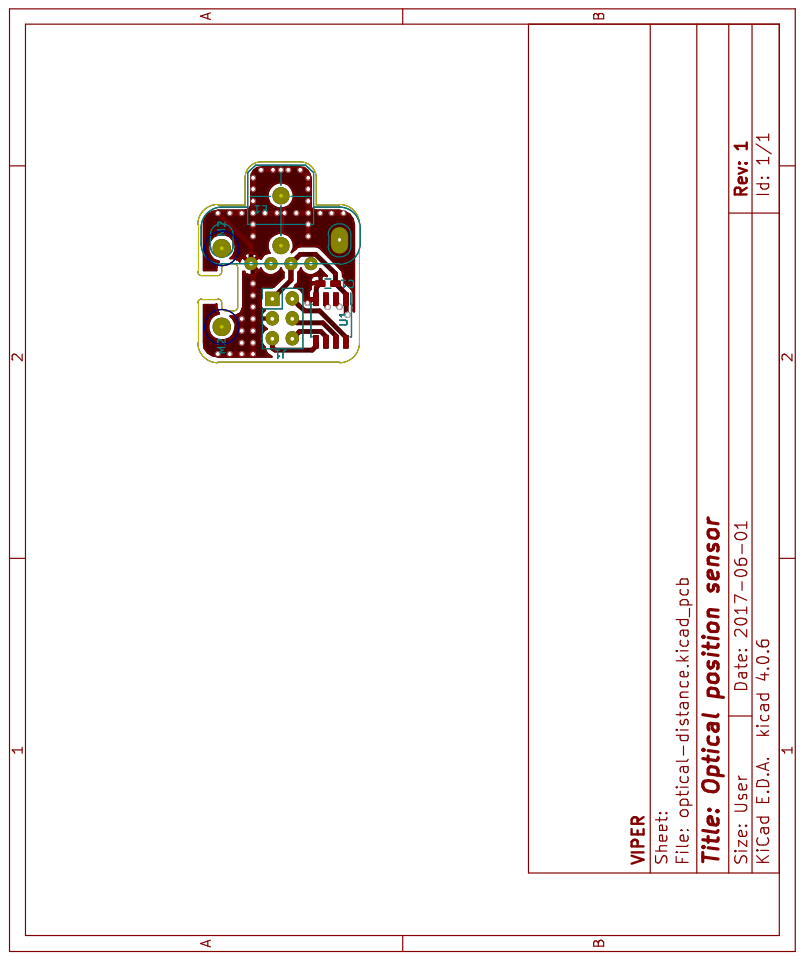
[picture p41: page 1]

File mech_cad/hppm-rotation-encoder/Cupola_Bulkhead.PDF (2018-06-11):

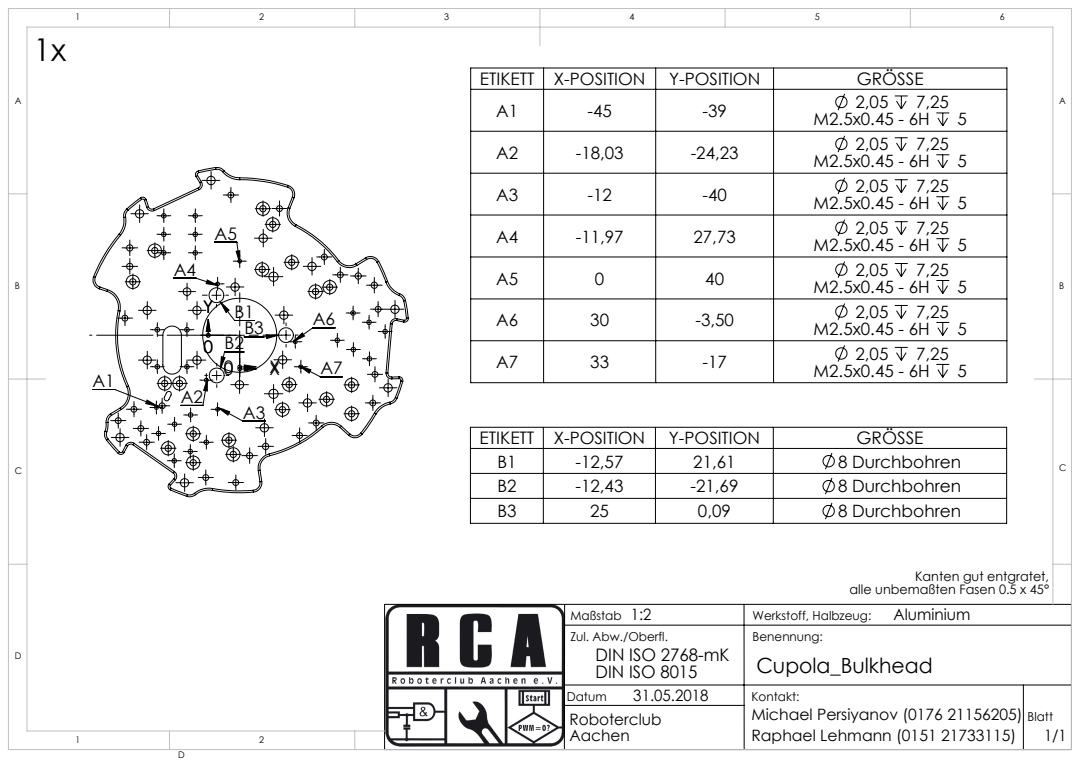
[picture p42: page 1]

ETIKETT | X-POSITION | Y-POSITION | GRÖSSE
A1 | -45 | -39 | 2,05 7,25 M2.5x0.45 - 6H 5
A2 | -18,03 | -24,23 | 2,05 7,25 M2.5x0.45 - 6H 5
A3 | -12 | -40 | 2,05 7,25 M2.5x0.45 - 6H 5
A4 | -11,97 | 27,73 | 2,05 7,25 M2.5x0.45 - 6H 5
A5 | 0 | 40 | 2,05 7,25 M2.5x0.45 - 6H 5
A6 | 30 | -3,50 | 2,05 7,25 M2.5x0.45 - 6H 5
A7 | 33 | -17 | 2,05 7,25 M2.5x0.45 - 6H 5

B1 | -12,57 | 21,61 | 8 Durchbohren
B2 | -12,43 | -21,69 | 8 Durchbohren
B3 | 25 | 0,09 | 8 Durchbohren

Kanten gut entgratet,

alle unbemaßten Fasen 0.5 x 45°

Maßstab 1:2 | Werkstoff, Halbzeug: Aluminium
Zul. Abw./Oberfl. DIN ISO 2768-mK DIN ISO 8015 | Benennung: Cupola_Bulkhead

31.05.2018 Datum | Kontakt: Michael Persiyanov (0176 21156205) Raphael Lehmann (0151 21733115) | Blatt 1/1

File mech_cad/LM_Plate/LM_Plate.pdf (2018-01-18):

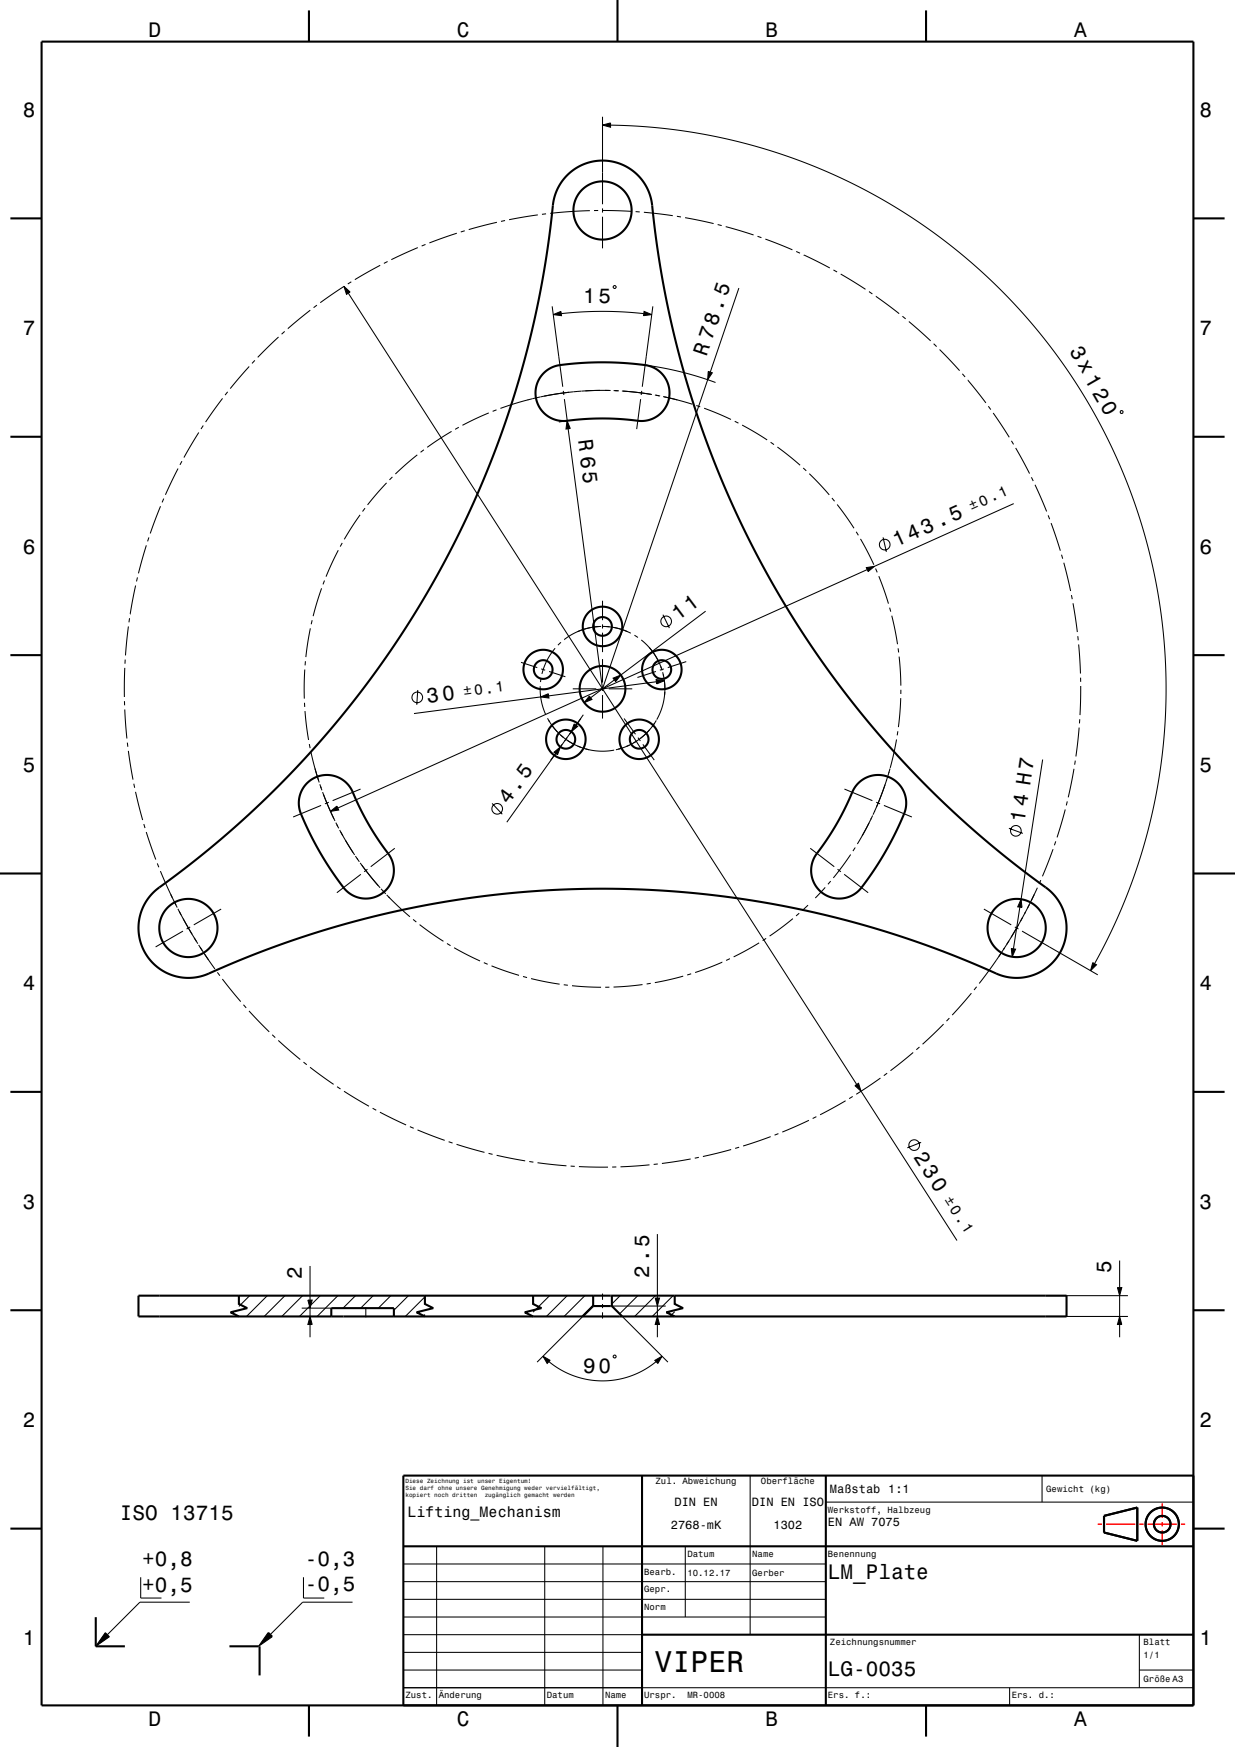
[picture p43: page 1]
kopiert noch dritten zugänglich gemacht werden; Maßstab; Gewicht (kg); Zul. Abweichung; Oberfläche; Größe A3; Werkstoff, Halbzeug; Zust.; Änderung; Datum; Name; Urspr.; Ers. f.:; Ers. d.:; Lifting_Mechanism; DIN EN; ISO 13715

Diese Zeichnung ist unser Eigentum!
Sie darf ohne unsere Genehmigung weder vervielfältigt,

DIN EN ISO

Datum | Name | Benennung LM_Plate

Bearb. | 10.12.17 | Gerber
Gepr.
Norm

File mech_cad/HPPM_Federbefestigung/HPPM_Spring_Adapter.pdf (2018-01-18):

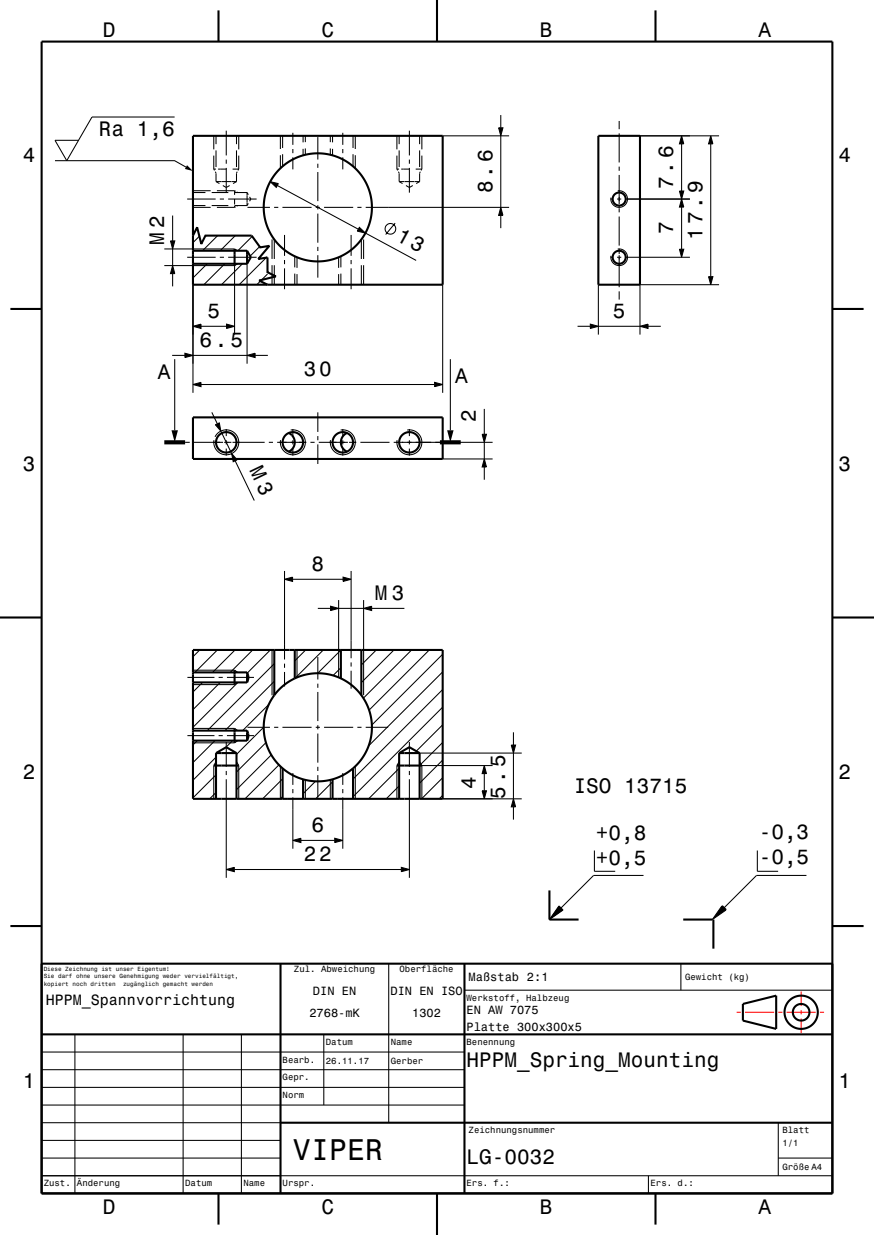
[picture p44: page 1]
kopiert noch dritten zugänglich gemacht werden; Maßstab; Gewicht (kg); Zul. Abweichung; Oberfläche; Größe A4; Werkstoff, Halbzeug; Zust.; Änderung; Datum; Name; Urspr.; Ers. f.:; Ers. d.:; HPPM_Spannvorrichtung; DIN EN; EN AW 7075 Platte 300x300x5; ISO 13715

Diese Zeichnung ist unser Eigentum!
Sie darf ohne unsere Genehmigung weder vervielfältigt,

DIN EN ISO

Datum | Name | Benennung HPPM_Spring_Mounting

Bearb. | 26.11.17 | Gerber
Gepr.
Norm

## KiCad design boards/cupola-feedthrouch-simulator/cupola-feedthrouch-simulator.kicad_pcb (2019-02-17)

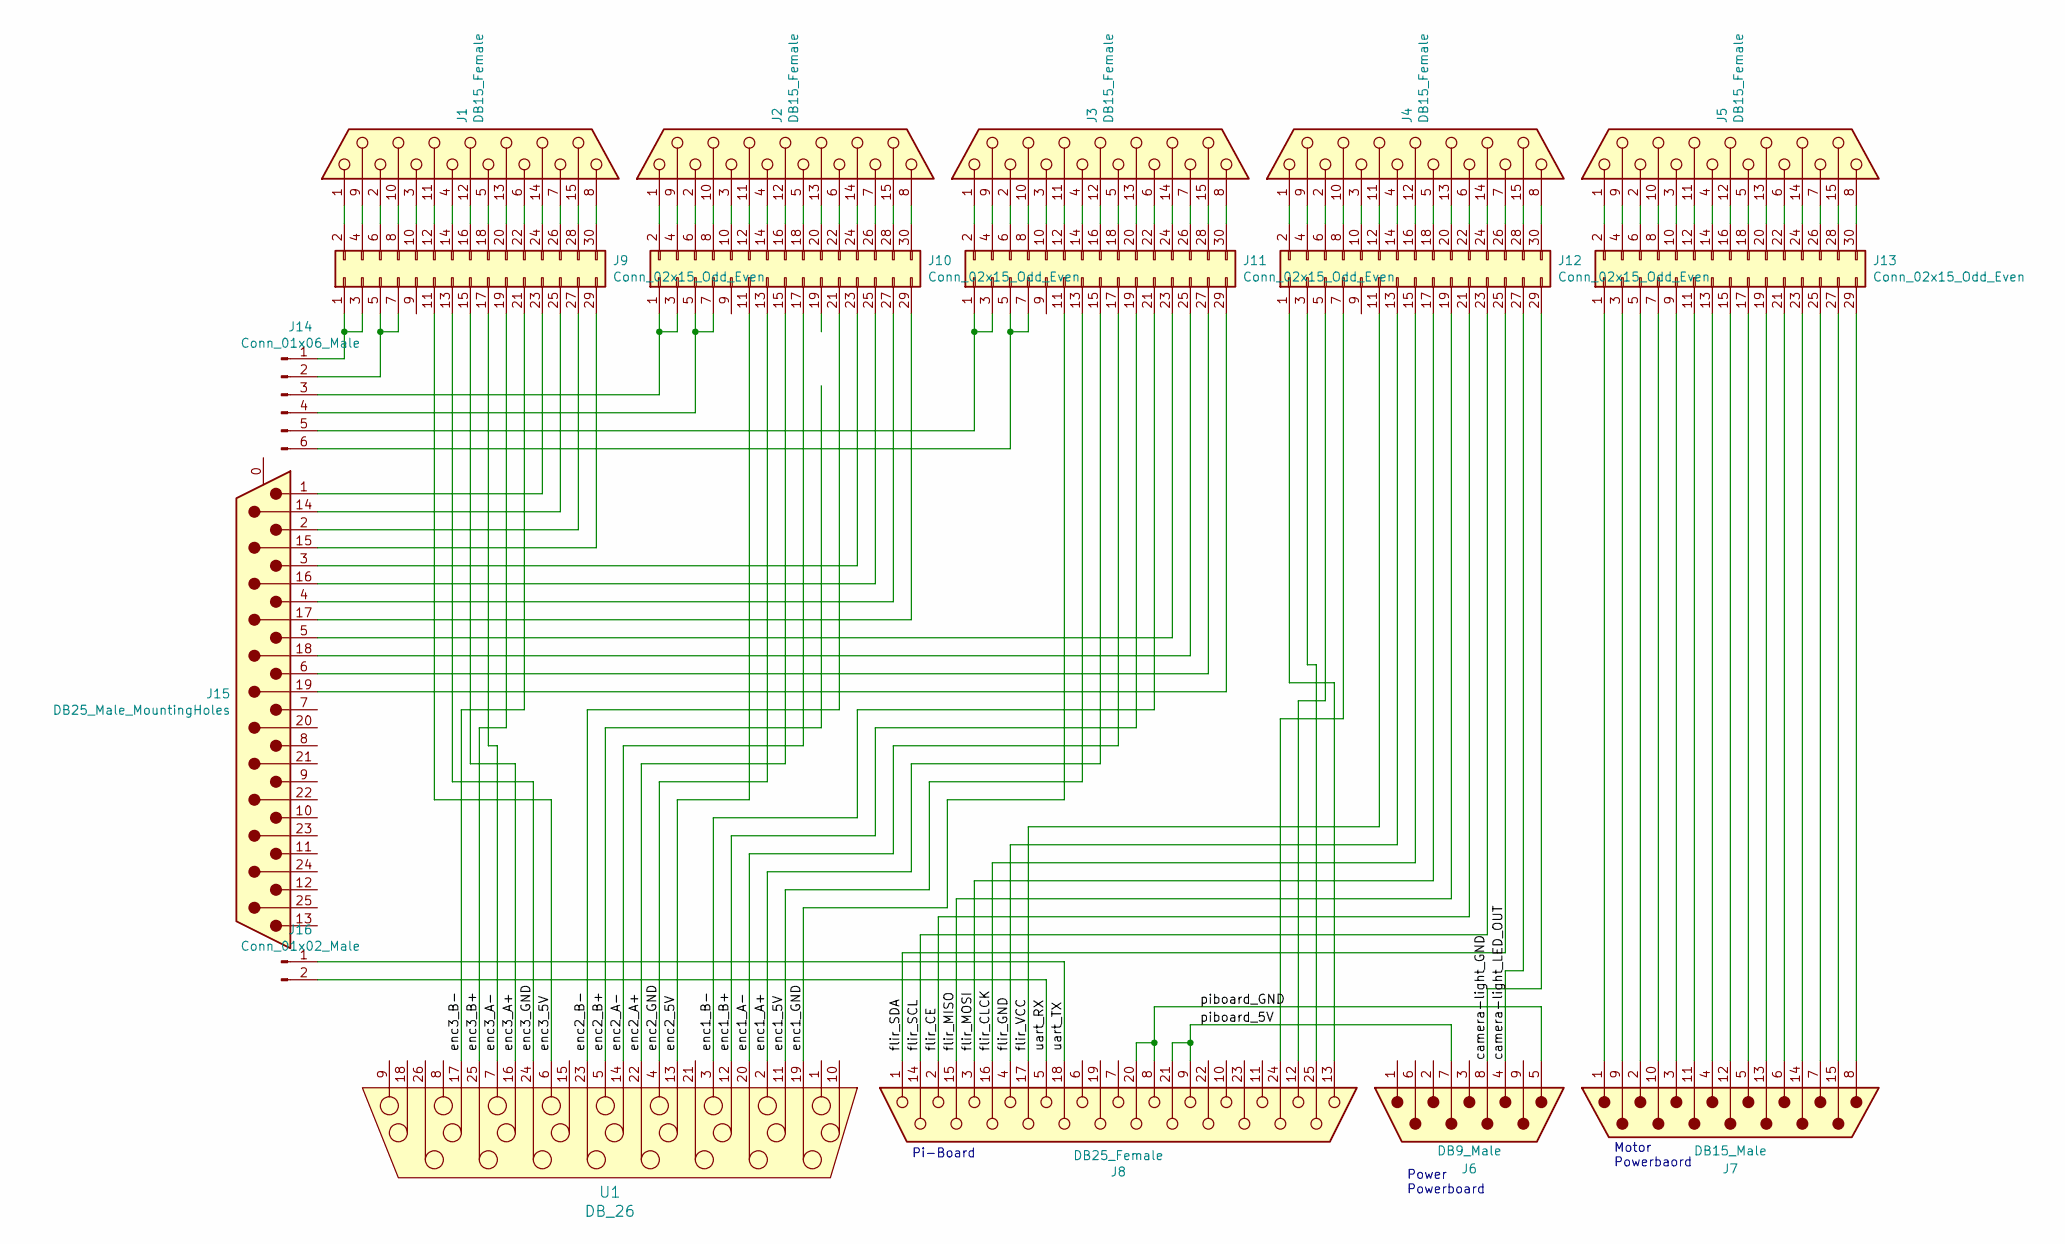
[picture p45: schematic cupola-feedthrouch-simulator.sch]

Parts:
J1, J2, J3, J4, J5: DB15_Female; DSUB-15_Female_Vertical_P2.77x2.84mm_MountingHoles
J6: DB9_Male; DSUB-9_Male_Vertical_P2.77x2.84mm_MountingHoles
J7: DB15_Male; DSUB-15_Male_Vertical_P2.77x2.84mm_MountingHoles
J8: DB25_Female; DSUB-25_Female_Vertical_P2.77x2.84mm_MountingHoles
J9, J10, J11, J12, J13: Conn_02x15_Odd_Even; PinHeader_2x15_P2.54mm_Vertical
J14: Conn_01x06_Male; PinHeader_1x06_P2.54mm_Vertical
J15: DB25_Male_MountingHoles; DSUB-25_Male_Vertical_P2.77x2.84mm_MountingHoles
J16: Conn_01x02_Male; PinHeader_1x02_P2.54mm_Vertical
U1: DB_26; DSUB-26-HD_Male_Vertical_P2.29x1.98mm_MountingHoles

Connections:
/camera-light_GND: J6.8, J12.29
/camera-light_LED_OUT: J6.4, J12.27
/enc1_5V: J11.13, U1.11
/enc1_A+: J11.15, U1.2
/enc1_A-: J11.17, U1.20
/enc1_B+: J11.19, U1.12
/enc1_B-: J11.21, U1.3
/enc1_GND: J11.11, U1.19
/enc2_5V: J10.11, U1.13
/enc2_A+: J10.15, U1.22
/enc2_A-: J10.17, U1.14
/enc2_B+: U1.5
/enc2_B-: J10.21, U1.23
/enc2_GND: J10.13, U1.4
/enc3_5V: J9.11, U1.6
/enc3_A+: J9.15, U1.16
/enc3_A-: J9.17, U1.7
/enc3_B+: J9.19, U1.25
/enc3_B-: J9.21, U1.17
/enc3_GND: J9.13, U1.24
/flir_CE: J8.2, J12.21
/flir_CLCK: J8.16, J12.15
/flir_GND: J8.4, J12.13
/flir_MISO: J8.15, J12.19
/flir_MOSI: J8.3, J12.17
/flir_SCL: J8.14, J12.23
/flir_SDA: J8.1, J12.25
/flir_VCC: J8.17, J12.11
/piboard_5V: J6.7, J8.9, J8.21
/piboard_GND: J6.5, J8.8, J8.20
/uart_RX: J8.5, J16.2
/uart_TX: J8.18, J16.1
unnamed: J1.1, J9.2
unnamed: J1.2, J9.6
unnamed: J1.3, J9.10
unnamed: J1.4, J9.14
unnamed: J1.5, J9.18
unnamed: J1.6, J9.22
unnamed: J1.7, J9.26
unnamed: J1.8, J9.30
unnamed: J1.9, J9.4
unnamed: J1.10, J9.8
unnamed: J1.11 (P111), J9.12
unnamed: J1.12, J9.16
unnamed: J1.13, J9.20
unnamed: J1.14, J9.24
unnamed: J1.15, J9.28
unnamed: J10.1, J10.3, J14.3
unnamed: J2.1, J10.2
unnamed: J2.9, J10.4
unnamed: J10.5, J10.7, J14.4
unnamed: J2.2, J10.6
unnamed: J2.10, J10.8
unnamed: J2.3, J10.10
unnamed: J2.11 (P111), J10.12
unnamed: J2.4, J10.14
unnamed: J2.12, J10.16
unnamed: J2.5, J10.18
unnamed: J2.13, J10.20
unnamed: J2.6, J10.22
unnamed: J10.23, J15.3
unnamed: J2.14, J10.24
unnamed: J10.25, J15.16
unnamed: J2.7, J10.26
unnamed: J10.27, J15.4
unnamed: J2.15, J10.28
unnamed: J10.29, J15.17
unnamed: J2.8, J10.30
unnamed: J11.1, J11.3, J14.5
unnamed: J3.1, J11.2
unnamed: J3.9, J11.4
unnamed: J11.5, J11.7, J14.6
unnamed: J3.2, J11.6
unnamed: J3.10, J11.8
unnamed: J3.3, J11.10
unnamed: J3.11 (P111), J11.12
unnamed: J3.4, J11.14
unnamed: J3.12, J11.16
unnamed: J3.5, J11.18
unnamed: J3.13, J11.20
unnamed: J3.6, J11.22
unnamed: J11.23, J15.5
unnamed: J3.14, J11.24
unnamed: J11.25, J15.18
unnamed: J3.7, J11.26
unnamed: J11.27, J15.6
unnamed: J3.15, J11.28
unnamed: J11.29, J15.19
unnamed: J3.8, J11.30
unnamed: J8.13, J12.1
unnamed: J4.1, J12.2
unnamed: J8.25, J12.3
unnamed: J4.9, J12.4
unnamed: J8.12, J12.5
unnamed: J4.2, J12.6
unnamed: J8.24, J12.7
unnamed: J4.10, J12.8
unnamed: J4.3, J12.10
unnamed: J4.11 (P111), J12.12
unnamed: J4.4, J12.14
unnamed: J4.12, J12.16
unnamed: J4.5, J12.18
unnamed: J4.13, J12.20
unnamed: J4.6, J12.22
unnamed: J4.14, J12.24
unnamed: J4.7, J12.26
unnamed: J4.15, J12.28
unnamed: J4.8, J12.30
unnamed: J7.1, J13.1
unnamed: J5.1, J13.2
unnamed: J7.9, J13.3
unnamed: J5.9, J13.4
unnamed: J7.2, J13.5
unnamed: J5.2, J13.6
unnamed: J7.10, J13.7
unnamed: J5.10, J13.8
unnamed: J7.3, J13.9
unnamed: J5.3, J13.10
unnamed: J7.11 (P111), J13.11
unnamed: J5.11 (P111), J13.12
unnamed: J7.4, J13.13
unnamed: J5.4, J13.14
unnamed: J7.12, J13.15
unnamed: J5.12, J13.16
unnamed: J7.5, J13.17
unnamed: J5.5, J13.18
unnamed: J7.13, J13.19
unnamed: J5.13, J13.20
unnamed: J7.6, J13.21
unnamed: J5.6, J13.22
unnamed: J7.14, J13.23
unnamed: J5.14, J13.24
unnamed: J7.7, J13.25
unnamed: J5.7, J13.26
unnamed: J7.15, J13.27
unnamed: J5.15, J13.28
unnamed: J7.8, J13.29
unnamed: J5.8, J13.30
unnamed: J9.1, J9.3, J14.1
unnamed: J9.5, J9.7, J14.2
unnamed: J9.23, J15.1
unnamed: J9.27, J15.2
unnamed: J9.25, J15.14
unnamed: J9.29, J15.15

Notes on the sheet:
Motor Powerbaord
Power Powerboard
Pi-Board

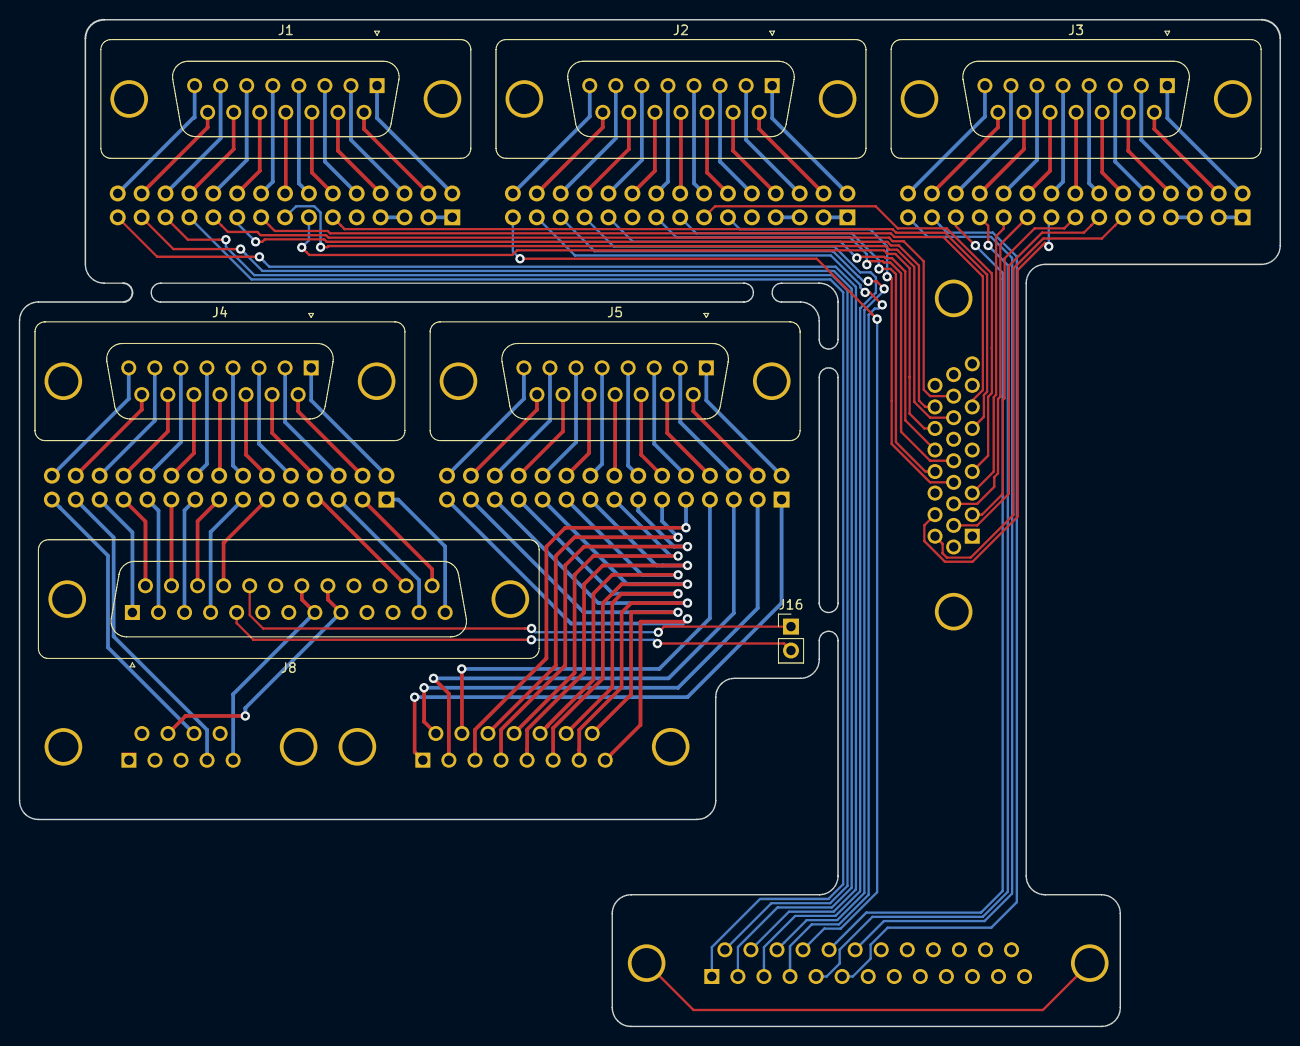
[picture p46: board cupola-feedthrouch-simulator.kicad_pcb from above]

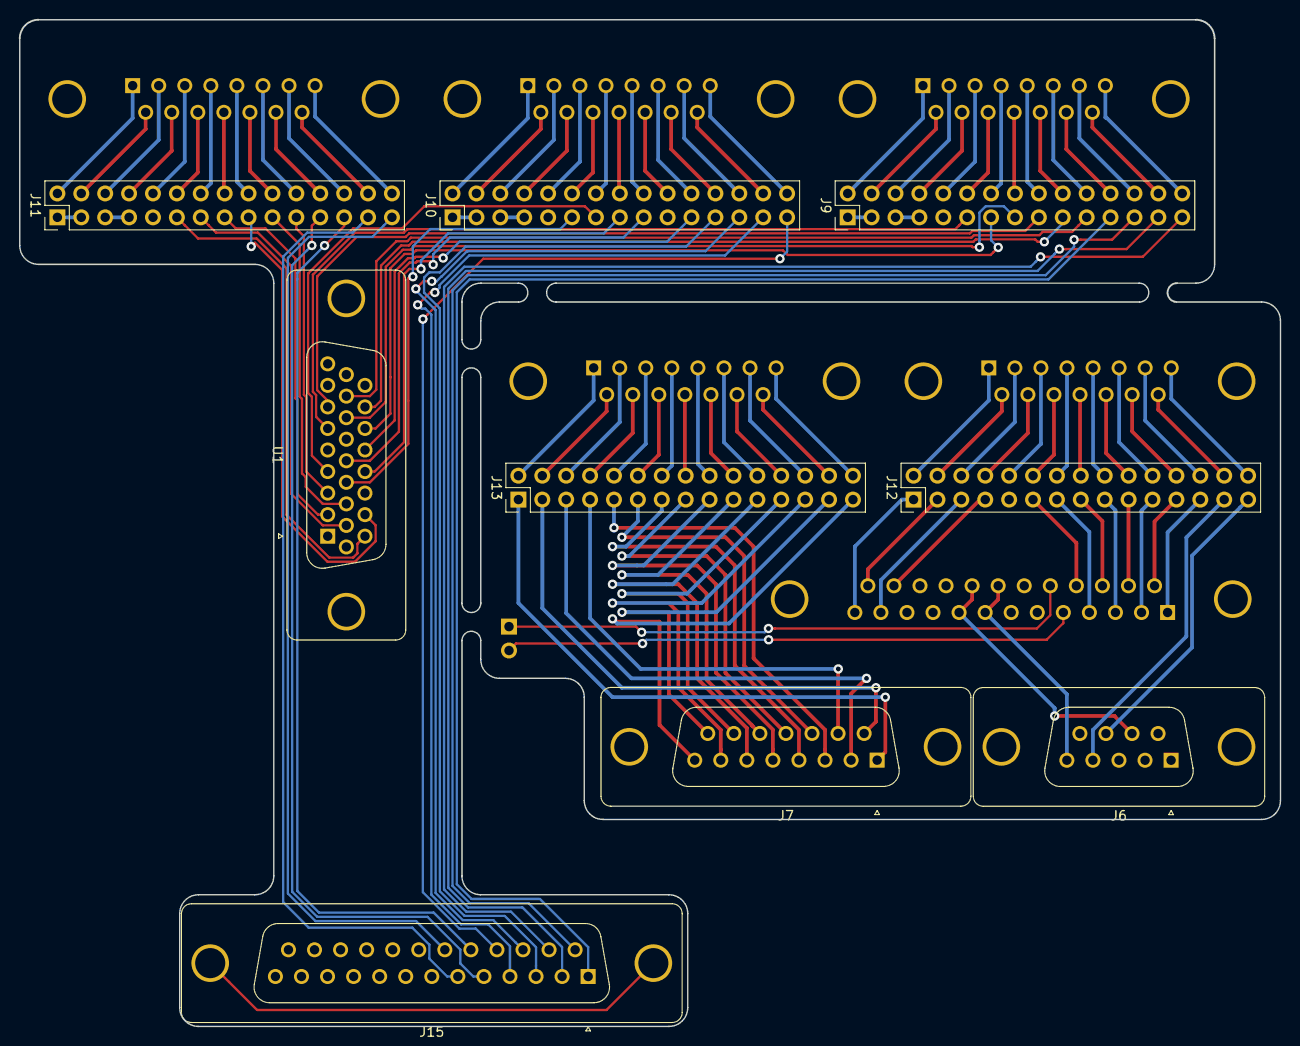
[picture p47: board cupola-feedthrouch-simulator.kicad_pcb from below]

Board: 2 copper layers, 134.0 x 107.0 mm, 16 parts (9 on the bottom side), 143 nets.

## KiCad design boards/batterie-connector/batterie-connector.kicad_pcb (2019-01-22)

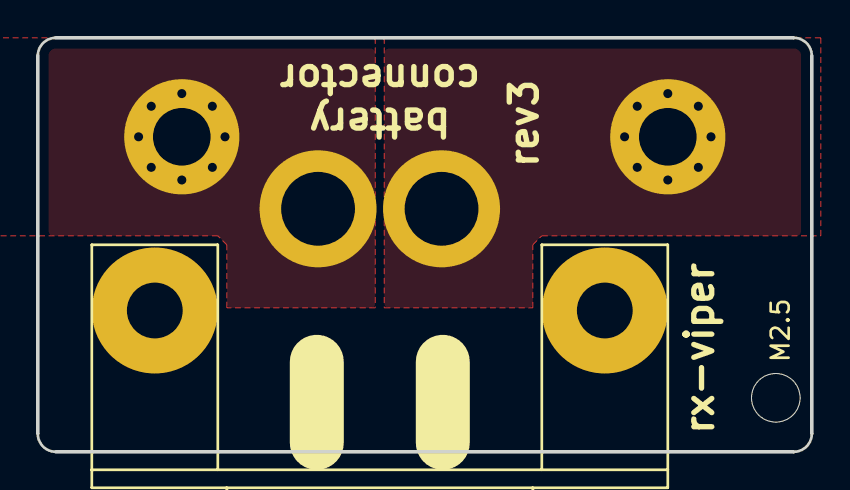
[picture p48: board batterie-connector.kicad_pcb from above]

Board: 2 copper layers, 43.0 x 23.0 mm, 4 parts (0 on the bottom side), 2 nets, no tracks yet.

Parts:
H101: M2.5; MountingHole_2.7mm_M2.5_DIN965
J101: 2W2C; D-Sub-Combo_2W2C
J102: +; MountingHole_3.2mm_M3_Pad_Via
J103: -; MountingHole_3.2mm_M3_Pad_Via

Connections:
/MINUS: J101.2, J103.1
/PLUS: J101.1, J102.1

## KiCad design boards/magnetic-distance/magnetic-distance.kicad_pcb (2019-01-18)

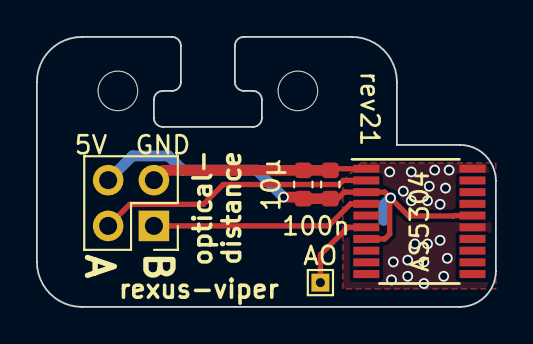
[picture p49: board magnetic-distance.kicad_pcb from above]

Board: 2 copper layers, 25.5 x 15.0 mm, 8 parts (1 on the bottom side), 5 nets.

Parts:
C101: 100n; C_0603_1608Metric
C102: 10µ; C_0603_1608Metric
H101, H102: M2; MountingHole_2.2mm_M2
J101: Cable; PinHeader_2x02_P2.54mm_Vertical
R_HEAT101: 100; R_0805_2012Metric
TP101: AO; TestPoint_THTPad_1.0x1.0mm_Drill0.5mm
U101: AS5304; TSSOP-20_4.4x6.5mm_P0.65mm

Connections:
+5V: C101.1, C102.1, J101.4, R_HEAT101.1, U101.3, U101.7, U101.16
/A: J101.2, U101.2
/AO: TP101.1, U101.6
/B: J101.1, U101.4
GND: C101.2, C102.2, J101.3, R_HEAT101.2, U101.1, U101.15, U101.20

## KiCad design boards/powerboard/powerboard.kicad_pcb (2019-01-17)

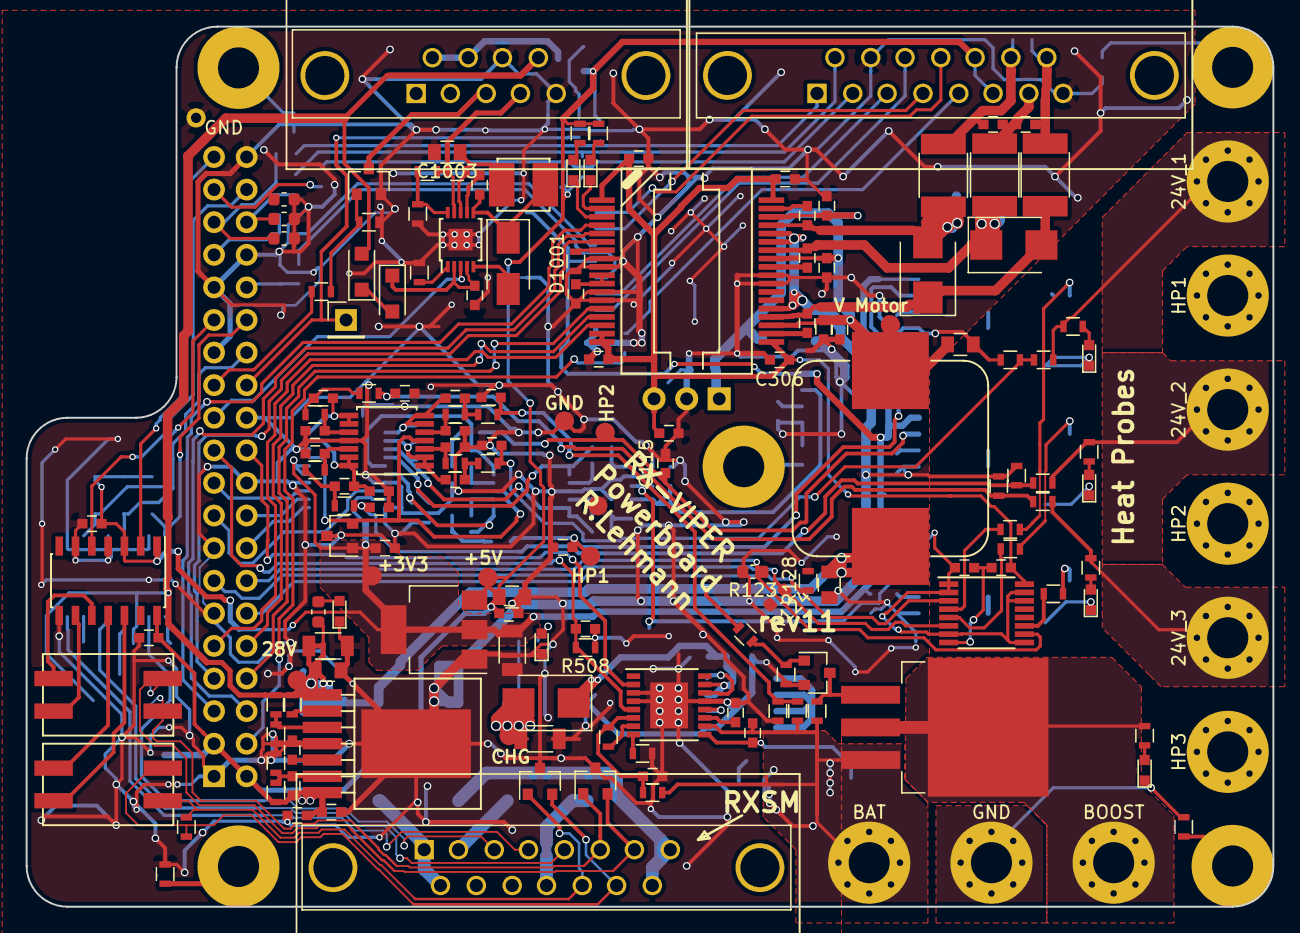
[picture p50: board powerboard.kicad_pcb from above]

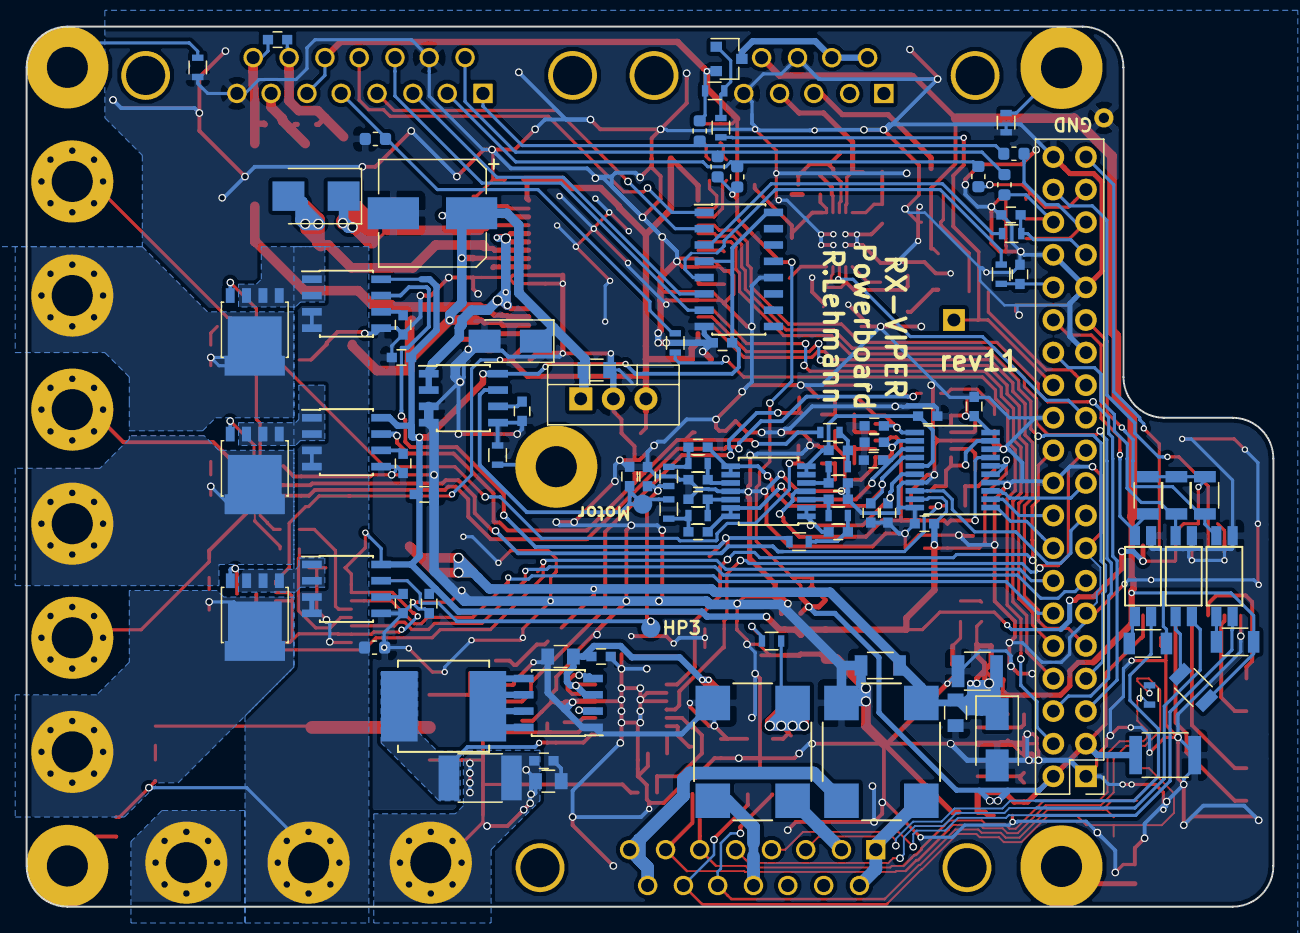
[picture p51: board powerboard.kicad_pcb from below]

Board: 2 copper layers, 97.2 x 68.6 mm, 268 parts (97 on the bottom side), 174 nets.

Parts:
C101: 10µ; C_1206
C102: 4µ7 1206 50V; C_1206
C103: 1µ; C_0805
C104: 10µ oder 4µ7 Tantal; C_0805
C105, C109, C302, C304, C305, C306, C308, C309, C310, C312, C315, C504, C506, C701, C801, C802, C803, C901, C902, C1002, C1201, C1202: 100n; C_0603
C106: 470n; C_0805
C107, C121: 2n7; C_0603
C108: 22µ Tantal; C_1206
C110, C111, C112, C113, C114, C115, C116, C117, C205, C910, C911, C912, C913, C914, C915, C916, C917: 10n; C_0603
C118: 10µ 1210; C_1210
C119: 1µ 0805 50V; C_0805
C120: 50SVPK68M; CP_Elec_8x10.5
C122, C123, C124: 22n; C_0603_1608Metric
C201: 10µ/40V; C_1206
C202: 1µ/40V; C_0805
C203, C204: 22n; C_0603
C206: 100µ/10V; C_1812
C207, C307, C314, C702, C1001: 1µ; C_0603
C301: 4µ7 0805; C_0805
C303: 10µ; C_0603
C313: 4µ7 0805; C_0603
C316, C317, C318: 100p; C_0603
C319, C804, C805, C806: 1n; C_0603
C501: 68n; C_0603
C502: 47n; C_0603
C503: 10µ 0805 35V; C_0805
C505: 10µ; C_0805
C507: 470n; C_0603
C508, C1101, C1102, C1103, C1104, C1105, C1106, C1107, C1108, C1109, C1110, C1111, C1112, C1113, C1114, C1115, C1116: 220n; C_0603
C1003: 4µ7 0805 50V; C_0805
D101: RX-PW; LED_0603
D102: RX-CHG; LED_0603
D103: BAT; LED_0603
D104, D105: SMAJ36A; D_SMA
D301, D302: LED; LED_0603
D304, D305, D306: SMBJ40CA; D_SMB_Standard
D501: MBRS360BT3G; D_SMB_Standard
D701, D702: ESD; SOT-23
D801: HP1; LED_0603
D802: HP2; LED_0603
D803: HP3; LED_0603
D1001: MBRA140T3; D_SMA_Standard
D1002, D1003: US1NWF; D_SOD-123F
FL101, FL102: 744272471; WE-SL5
FL701, FL702: 744228; WE-SL2
J101: RXSM experiment connector; DB15MD
J102: Powerboard <-> Mainboard; Pin_Header_Straight_2x20_Pitch2.54mm
J103: Cameraboard; DB9FD
J104: BLDC Motor; DB15FD
J105: BOOST; MountingHole_3.2mm_M3_Pad_Via
J106: Boost24V_EN; Pin_Header_Straight_1x01_Pitch2.54mm
J107: 24V_1; MountingHole_3.2mm_M3_Pad_Via
J108: 24V_2; MountingHole_3.2mm_M3_Pad_Via
J109: 24V_3; MountingHole_3.2mm_M3_Pad_Via
J110: BAT; MountingHole_3.2mm_M3_Pad_Via
J111: GND; MountingHole_3.2mm_M3_Pad_Via
J112, J113, J114, J115, J117: M3; MountingHole_3.2mm_M3_Pad
J810: HP1; MountingHole_3.2mm_M3_Pad_Via
J811: HP2; MountingHole_3.2mm_M3_Pad_Via
J812: HP3; MountingHole_3.2mm_M3_Pad_Via
L101: Coilcraft MSS1583-474; L_Coilcraft_1583_Handsoldering
L301, L302, L303: 742792515; L_1812
L501: Coilcraft XAL6060-223; L_Coilcraft_XAL60xx_Handsoldering
L1001: Coilcraft XAL4040-103; L_Coilcraft_XAL40xx_Handsoldering
Q101: SQM40031EL; TO-263-3Lead
Q102: DMN6140L; SOT-23
Q103: PMV27UPE; SOT-23
Q104: PMV55ENEA; SOT-23
Q503: IRF7343PBF; SOIC-8_3.9x4.9mm_Pitch1.27mm
Q801, Q802, Q803: BUK7Y4R8-60E; SOT-669_LFPAK
R101, R103, R126, R128, R508, R801, R802, R803, R807, R808, R809: 10k; R_0603
R102: 20k; R_0603
R104: 91k; R_0603
R105: 13k; R_0603
R106, R108, R113: 15k; R_0603
R107, R109, R110, R114, R130, R607, R608: 1k; R_0603
R111: 0; R_0603
R112, R129, R1002: 100k; R_0603
R115, R116, R117, R118, R120: NC; R_0603
R119, R121: 100; R_0603
R122: 0; R_0603_1608Metric
R123, R124, R125: 10k; R_0603_1608Metric
R127: 4k; R_0603
R131, R132, R133, R137: 4k7; R_0603_1608Metric
R134, R135, R136: 470; R_0603_1608Metric
R201: 68k1; R_0603
R202: 11k8; R_0603
R203: 43k2; R_0603
R204: 5k62; R_0603
R205: 1k07; R_0603
R301, R302: 470; R_0603
R303: 200k; R_0603
R504: 65k7; R_0603
R505: 8k2; R_0603
R506: 50k; R_0603
R507: 100m; R_1812
R601, R602, R603, R604, R605, R606: 10k 1206; R_1206
R1001: 140k; R_0603
R1003: 4k7; R_0603
R1004: 2R; R_0603
R1101, R1102, R1103, R1104, R1105, R1106, R1107, R1108, R1109, R1110, R1111, R1112, R1113, R1114, R1115, R1116: 47k; R_0603
TP101: 28V; Measurement_Point_Round-SMD-Pad_Small
TP102: CHG; Measurement_Point_Round-SMD-Pad_Small
TP103: +5V; Measurement_Point_Round-SMD-Pad_Small
TP104: +3V3; Measurement_Point_Round-SMD-Pad_Small
TP105, TP106: GND; Measurement_Point_Round-SMD-Pad_Small
TP107: HP3C; Measurement_Point_Round-SMD-Pad_Small
TP108: GND; Measurement_Point_Round-TH_Small
TP109: HP2C; Measurement_Point_Round-SMD-Pad_Small
TP110: HP1C; Measurement_Point_Round-SMD-Pad_Small
TP111: V_MOTOR; Measurement_Point_Round-SMD-Pad_Small
TP112: MOTORC; Measurement_Point_Round-SMD-Pad_Small
U101: LM1117-3.3; SOT-223
U102: DS26LV32AT; SOIC-16_3.9x9.9mm_Pitch1.27mm
U201: LMZ14203; 7TO-PMOD
U301: 7812SR-C; TO-220_Vertical
U302: DRV8332; HSSOP-36
U303, U801, U802, U803: ACS711; SOIC-8_3.9x4.9mm_Pitch1.27mm
U501: LTC4010; TSSOP-16-1EP_4.4x5mm_Pitch0.65mm
U601, U602, U603: PC3H7; SOP-4
U701: MAX13432EESD; SOIC-14_3.9x8.7mm_Pitch1.27mm
U901: AD7928; TSSOP-20_4.4x6.5mm_Pitch0.65mm
U902: REF3025; SOT-23
U1001: LT3592; MSOP-10-1EP_3x3mm_Pitch0.5mm
U1101, U1102: LMV324; TSSOP-14_4.4x5mm_Pitch0.65mm
U1201: CD40109B; TSSOP-16_4.4x5mm_Pitch0.65mm

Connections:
+2V5: U901.7, U902.2, U1101.4, U1102.4
+3V3: C108.1, C109.1, C701.1, C801.1, C802.1, C803.1, C901.1, C902.1, C1201.1, R601.2, R602.2, R603.2, TP104.1, U101.2, U101.4, U102.4, U102.16, U303.8, U701.1, U701.3, U801.8, U802.8, U803.8, U901.5, U901.6, U901.19, U902.1, U1201.1, U1201.2, U1201.7, U1201.9, U1201.14, U1201.15
+5V: C104.1, C105.1, C204.1, C205.1, C206.1, C207.1, C702.1, J102.2, J102.3, J104.6, J104.13, Q103.2, R129.2, R131.1, R132.1, R133.1, R204.1, R301.2, R302.2, TP103.1, U101.3, U201.7, U701.14
+12V: C302.1, C303.1, C304.1, C306.1, C312.1, C1202.1, U301.3, U302.1, U302.17, U302.18, U302.19, U302.36, U1201.16
/24V_BAT_1: J107.1, R113.1, R807.2
/24V_BAT_2: J108.1, R108.1, R808.2
/24V_BAT_3: J109.1, R106.1, R809.2
/BAT_10V: J105.1, Q101.2, R127.2
/BAT_raw: C505.1, C506.1, C507.1, J110.1, Q101.3, R101.1, R104.1, R504.1, R507.2, U501.10
/Boost24V_EN: J102.26, J106.1, R130.2
/Cam_Light_EN: J102.23, U1001.3
/Charge_EN: C501.1, J102.21, R508.2, U501.5
/Charge_status: J102.22, U501.2
/Encoder_A: C107.1, J102.32, R119.1
/Encoder_A+: J104.3, U102.6
/Encoder_A-: J104.11, U102.7
/Encoder_A_filter: R119.2, U102.5
/Encoder_B: C121.1, J102.33, R121.1
/Encoder_B+: J104.4, U102.2
/Encoder_B-: J104.12, U102.1
/Encoder_B_filter: R121.2, U102.3
/EndSwitch: J102.4, R111.1
/Hall_U: J104.1, R133.2, R134.1
/Hall_U_filter: C122.1, J102.35, R134.2
/Hall_V: J104.9, R132.2, R135.1
/Hall_V_filter: C123.1, J102.36, R135.2
/Hall_W: J104.2, R131.2, R136.1
/Hall_W_filter: C124.1, J102.37, R136.2
/LO: J102.28, R601.1, U601.4
/Lens_Heat_EN: J102.25, R110.2
/Motor1_Current: C117.1, R1104.2, TP112.1, U303.7
/Motor_U_N: J102.6, U302.5
/Motor_U_P: J102.5, U302.4
/Motor_V_N: J102.8, U302.14
/Motor_V_P: J102.7, U302.6
/Motor_W_N: J102.10, U302.15
/Motor_W_P: J102.9, U302.16
/Phase_U: C317.1, C318.2, J104.14, L301.2
/Phase_V: C316.1, C317.2, J104.7, L302.2
/Phase_W: C316.2, C318.1, J104.15, L303.2
/Powerboard Battery Charging/bat_bgate: Q503.2, U501.12
/Powerboard Battery Charging/bat_inductor: L501.1, Q503.5, Q503.6, Q503.7, Q503.8
/Powerboard Battery Charging/bat_sense: C507.2, L501.2, R507.1, U501.9
/Powerboard Battery Charging/bat_tgate: Q503.4, U501.14
/Powerboard Battery Charging/charge_power: C101.1, D501.2, FL102.2, R126.2, TP102.1
/Powerboard Motor Controller/VREG: C305.1, U302.10, U302.11
/Powerboard Motor Controller/V_IN: C106.1, C120.1, C301.1, C307.1, C313.1, C314.1, C315.1, D105.1, L101.2, TP111.1, U301.1, U302.21, U302.29, U302.34
/Powerboard_ADC/IN0: C910.1, C1105.1, U901.16, U1101.1, U1101.2
/Powerboard_ADC/IN1: C911.1, C1106.1, U901.15, U1101.6, U1101.7
/Powerboard_ADC/IN2: C912.1, C1107.1, U901.14, U1101.8, U1101.9
/Powerboard_ADC/IN3: C913.1, C1108.1, U901.13, U1101.13, U1101.14
/Powerboard_ADC/IN4: C914.1, C1113.1, U901.12, U1102.1, U1102.2
/Powerboard_ADC/IN5: C915.1, C1114.1, U901.11, U1102.6, U1102.7
/Powerboard_ADC/IN6: C916.1, C1115.1, U901.10, U1102.8, U1102.9
/Powerboard_ADC/IN7: C917.1, C1116.1, U901.9, U1102.13, U1102.14
/Powerboard_ADC_Filter/IN4: C113.1, R113.2, R114.1, R1109.2
/Powerboard_ADC_Filter/IN5: C110.1, R104.2, R105.1, R1110.2
/Powerboard_ADC_Filter/IN6: C111.1, R106.2, R107.1, R1111.2
/Powerboard_ADC_Filter/IN7: C112.1, R108.2, R109.1, R1112.2
/Powerboard_Heat_Probes/Probe1: D801.1, J810.1, Q801.5
/Powerboard_Heat_Probes/Probe1_sense: Q801.1, Q801.2, Q801.3, U801.1, U801.2
/Powerboard_Heat_Probes/Probe2: D802.1, J811.1, Q802.5
/Powerboard_Heat_Probes/Probe2_sense: Q802.1, Q802.2, Q802.3, U802.1, U802.2
/Powerboard_Heat_Probes/Probe3: D803.1, J812.1, Q803.5
/Powerboard_Heat_Probes/Probe3_sense: Q803.1, Q803.2, Q803.3, U803.1, U803.2
/Powerboard_LED_driver/LED_OUT: J103.4, R1002.2, R1004.2, U1001.9
/Powerboard_MOSFET_Driver/OUT_A: R801.2, U1201.4
/Powerboard_MOSFET_Driver/OUT_B: R802.2, U1201.5
/Powerboard_MOSFET_Driver/OUT_C: R803.2, U1201.11
/Probe1_Current: C116.1, R1101.2, TP110.1, U801.7
/Probe1_EN: J102.12, R128.1, U1201.3
/Probe2_Current: C115.1, R1102.2, TP109.1, U802.7
/Probe2_EN: J102.13, R124.1, U1201.6
/Probe3_Current: C114.1, R1103.2, TP107.1, U803.7
/Probe3_EN: J102.14, R123.1, U1201.10
/RX: J102.39, U701.2
/RXSM_28V: C102.1, C103.1, C118.1, C119.1, C201.1, C202.1, D104.1, D1002.2, FL101.2, J103.9, L101.1, R102.2, R125.2, R201.1, R203.2, R604.1, R605.1, R606.1, TP101.1, U201.1
/RXSM_Ground: FL101.4, J101.8, J101.15
/RXSM_LO: J101.5, U601.2
/RXSM_RX_A: D702.1, FL701.2, J101.13, R608.1
/RXSM_RX_Y: D701.1, FL702.2, J101.6, R607.1
/RXSM_RX_~B: D702.2, FL701.3, J101.14, R608.2
/RXSM_RX_~Z: D701.2, FL702.3, J101.7, R607.2
/RXSM_SODS: J101.3, U603.2
/RXSM_SOE: J101.4, U602.2
/RXSM_charge+: FL102.1, J101.2
/RXSM_charge-: FL102.4, J101.12
/RXSM_power: FL101.1, J101.1, J101.9
/SODS: J102.30, R603.1, U603.4
/SOE: J102.29, R602.1, U602.4
/TX: J102.38, U701.5
/extADC_SPI_CS1: J102.19, U901.3
/extADC_SPI_MISO: J102.17, U901.18
/extADC_SPI_MOSI: J102.18, U901.2
/extADC_SPI_SCK: J102.16, U901.1
GND: C101.2, C102.2, C103.2, C104.2, C105.2, C106.2, C107.2, C108.2, C109.2, C110.2, C111.2, C112.2, C113.2, C114.2, C115.2, C116.2, C117.2, C118.2, C119.2, C120.2, C121.2, C122.2, C123.2, C124.2, C201.2, C202.2, C203.2, C205.2, C206.2, C207.2, C301.2, C302.2, C303.2, C304.2, C305.2, C306.2, C307.2, C312.2, C313.2, C314.2, C315.2, C319.2, C501.2, C502.2, C503.2, C504.2, C505.2, C506.2, C508.2, C701.2, C702.2, C801.2, C802.2, C803.2, C804.2, C805.2, C806.2, C901.2, C902.2, C910.2, C911.2, C912.2, C913.2, C914.2, C915.2, C916.2, C917.2, C1001.1, C1003.2, C1101.2, C1102.2, C1103.2, C1104.2, C1109.2, C1110.2, C1111.2, C1112.2, D101.1, D102.1, D104.2, D105.2, D701.3, D702.3, FL101.3, FL102.3, J102.1, J102.11, J102.15, J102.20, J102.24, J102.27, J102.31, J102.34, J102.40, J103.5, J103.8, J104.8, J104.10, Q102.2, Q104.2, Q503.1, R103.2, R105.2, R107.2, R109.2, R112.1, R114.2, R115.2, R116.2, R118.2, R120.2, R122.1, R123.2, R124.2, R128.2, R137.2, R202.2, R205.2, R303.2, R506.2, R508.1, R1001.2, R1003.2, TP105.1, TP106.1, TP108.1, U101.1, U102.8, U102.12, U201.4, U201.8, U301.2, U302.8, U302.9, U302.12, U302.13, U302.26, U302.27, U303.3, U303.4, U303.5, U501.3, U501.4, U501.13, U501.17, U601.3, U602.3, U603.3, U701.4, U701.6, U701.8, U801.5, U802.5, U803.5, U901.4, U901.8, U901.17, U901.20, U902.3, U1001.11, U1101.11, U1102.11
GNDPWR: C1201.2, C1202.2, D103.1, J111.1, R117.2, R122.2, U801.3, U801.4, U802.3, U802.4, U803.3, U803.4, U1201.8
unnamed: C203.1, U201.5
unnamed: C204.2, R204.2, R205.1, U201.6
unnamed: C308.1, D305.1, D306.2, L301.1, U302.33
unnamed: C308.2, U302.35
unnamed: C309.1, D304.1, D305.2, L302.1, U302.30
unnamed: C309.2, U302.28
unnamed: C310.1, D304.2, D306.1, L303.1, U302.22
unnamed: C310.2, U302.20
unnamed: C319.1, U303.6
unnamed: C502.1, R504.2, R505.2, U501.6
unnamed: C503.1, C508.1, D501.1, Q503.3, U501.15
unnamed: C504.1, U501.11
unnamed: C804.1, U801.6
unnamed: C805.1, U802.6
unnamed: C806.1, U803.6
unnamed: C1001.2, D1003.1, U1001.2, U1001.4
unnamed: C1002.1, D1001.1, L1001.1, U1001.6
unnamed: C1002.2, U1001.7
unnamed: C1003.1, L1001.2, R1004.1, U1001.8
unnamed: C1101.1, R1105.1, U1101.3
unnamed: C1102.1, R1106.1, U1101.5
unnamed: C1103.1, R1107.1, U1101.10
unnamed: C1104.1, R1108.1, U1101.12
unnamed: C1105.2, R1101.1, R1105.2
unnamed: C1106.2, R1102.1, R1106.2
unnamed: C1107.2, R1103.1, R1107.2
unnamed: C1108.2, R1104.1, R1108.2
unnamed: C1109.1, R1113.1, U1102.3
unnamed: C1110.1, R1114.1, U1102.5
unnamed: C1111.1, R1115.1, U1102.10
unnamed: C1112.1, R1116.1, U1102.12
unnamed: C1113.2, R1109.1, R1113.2
unnamed: C1114.2, R1110.1, R1114.2
unnamed: C1115.2, R1111.1, R1115.2
unnamed: C1116.2, R1112.1, R1116.2
unnamed: D101.2, R125.1
unnamed: D102.2, R126.1
unnamed: D103.2, R127.1
unnamed: D301.1, U302.2
unnamed: D301.2, R301.1
unnamed: D302.1, U302.3
unnamed: D302.2, R302.1
unnamed: D801.2, R807.1
unnamed: D802.2, R808.1
unnamed: D803.2, R809.1
unnamed: D1001.2, U1001.5
unnamed: D1002.1, D1003.2
unnamed: FL701.1, U701.12
unnamed: FL701.4, U701.11
unnamed: FL702.1, U701.9
unnamed: FL702.4, U701.10
unnamed: J103.3, Q104.3
unnamed: J103.6, J103.7, Q103.3
unnamed: J104.5, R111.2, R137.1
unnamed: J112.1, R115.1
unnamed: J113.1, R116.1
unnamed: J114.1, R117.1
unnamed: J115.1, R118.1
unnamed: J117.1, R120.1
unnamed: Q101.1, Q102.3, R101.2
unnamed: Q102.1, R102.1, R103.1
unnamed: Q103.1, R129.1, R130.1
unnamed: Q104.1, R110.1, R112.2
unnamed: Q801.4, R801.1
unnamed: Q802.4, R802.1
unnamed: Q803.4, R803.1
unnamed: R201.2, R202.1, U201.3
unnamed: R203.1, U201.2
unnamed: R303.1, U302.7
unnamed: R505.1, U501.7
unnamed: R506.1, U501.8
unnamed: R604.2, U603.1
unnamed: R605.2, U602.1
unnamed: R606.2, U601.1
unnamed: R1001.1, U1001.1
unnamed: R1002.1, R1003.1, U1001.10
unnamed: U302.23, U302.31, U302.32, U303.1, U303.2

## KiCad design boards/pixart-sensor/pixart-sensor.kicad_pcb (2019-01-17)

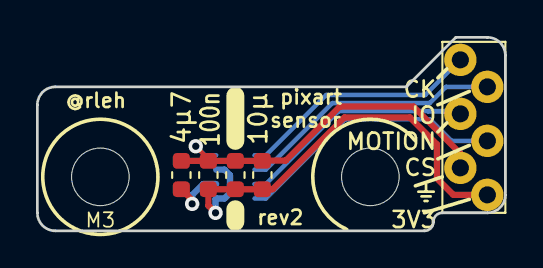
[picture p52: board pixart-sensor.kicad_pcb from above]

Board: 2 copper layers, 26.0 x 10.8 mm, 8 parts (1 on the bottom side), 7 nets.

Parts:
C101: 10µ; C_0603_1608Metric
C102: 100n; C_0603_1608Metric
C103: 4µ7; C_0603_1608Metric
H101, H102: M3; MountingHole_3.2mm_M3
J101: Adapter; PinHeader_Custom_2x03_Versetzt
R101: HEAT; R_0603_1608Metric
U101: PAT9125EL

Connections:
+3V3: C101.1, C102.1, J101.1, R101.1, U101.1, U101.3
/ID,~CS: J101.3, U101.8
/MOTION: J101.4, U101.7
/SCA,SDIO: J101.5, U101.6
/SCL,SCLK: J101.6, U101.5
GND: C101.2, C102.2, C103.2, J101.2, R101.2, U101.4
unnamed: C103.1, U101.2

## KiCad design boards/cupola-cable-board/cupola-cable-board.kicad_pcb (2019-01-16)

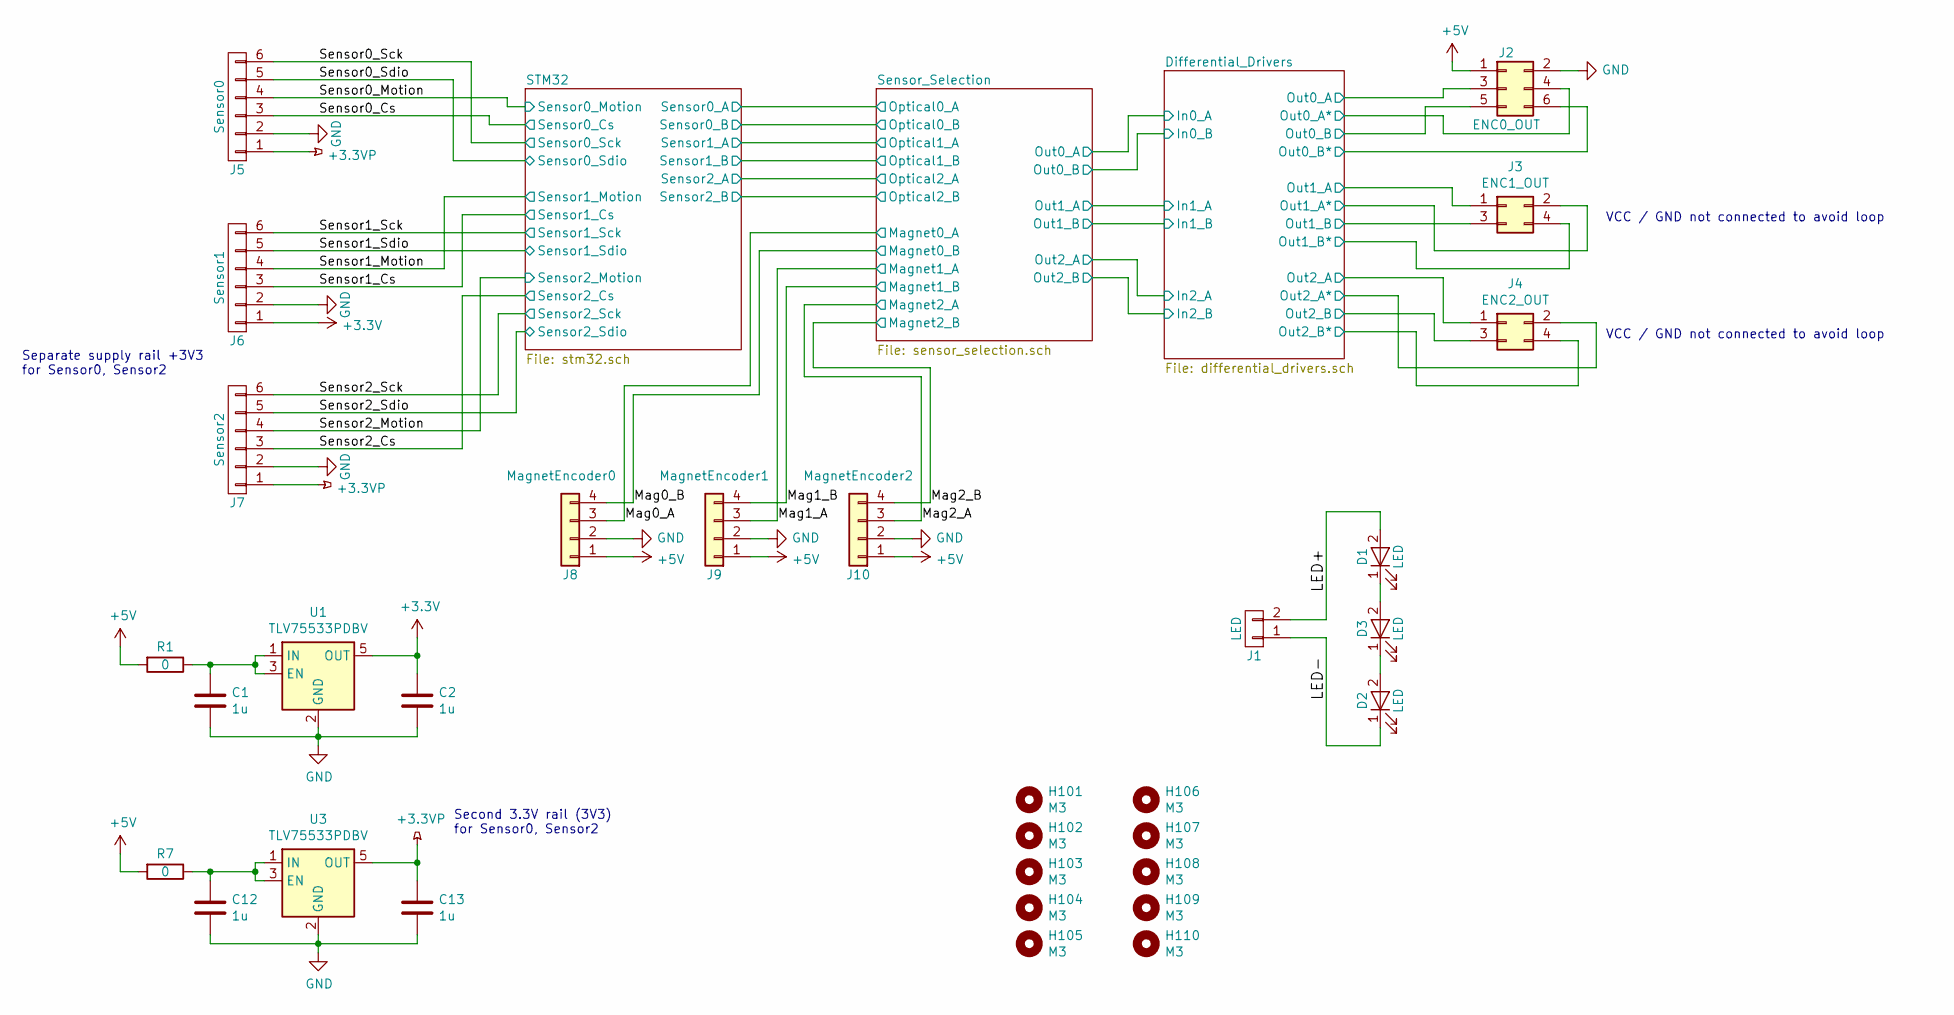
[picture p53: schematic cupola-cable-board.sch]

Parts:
C1, C2, C12, C13: 1u; C_0603_1608Metric
D1, D2, D3: LED; LW_G6SP_Handsoldering
H101, H102, H103, H104, H105, H106, H107, H108, H109, H110: M3; MountingHole_3.2mm_M3
J1: LED; PinHeader_1x02_P2.00mm_Vertical
J2: ENC0_OUT; PinHeader_2x03_P2.00mm_Vertical
J3: ENC1_OUT; PinHeader_2x02_P2.00mm_Vertical
J4: ENC2_OUT; PinHeader_2x02_P2.00mm_Vertical
J5: Sensor0; PinHeader_1x06_P2.00mm_Vertical
J6: Sensor1; PinHeader_1x06_P2.00mm_Vertical
J7: Sensor2; PinHeader_1x06_P2.00mm_Vertical
J8: MagnetEncoder0; PinHeader_1x04_P2.00mm_Vertical
J9: MagnetEncoder1; PinHeader_1x04_P2.00mm_Vertical
J10: MagnetEncoder2; PinHeader_1x04_P2.00mm_Vertical
R1, R7: 0; R_0603_1608Metric
U1, U3: TLV75533PDBV; SOT-23-5

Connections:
+3.3VP: C13.1, J5.1, J7.1, U3.5 (OUT)
+3V3: C2.1, J6.1, U1.5 (OUT); also elsewhere on the board
+5V: J2.1, J8.1, J9.1, J10.1, R1.2, R7.2; also elsewhere on the board
/Differential_Drivers/Out0_A: J2.3; also elsewhere on the board
/Differential_Drivers/Out0_A*: J2.4; also elsewhere on the board
/Differential_Drivers/Out0_B: J2.5; also elsewhere on the board
/Differential_Drivers/Out0_B*: J2.6; also elsewhere on the board
/Differential_Drivers/Out1_A: J3.1; also elsewhere on the board
/Differential_Drivers/Out1_A*: J3.2; also elsewhere on the board
/Differential_Drivers/Out1_B: J3.3; also elsewhere on the board
/Differential_Drivers/Out1_B*: J3.4; also elsewhere on the board
/Differential_Drivers/Out2_A: J4.1; also elsewhere on the board
/Differential_Drivers/Out2_A*: J4.2; also elsewhere on the board
/Differential_Drivers/Out2_B: J4.3; also elsewhere on the board
/Differential_Drivers/Out2_B*: J4.4; also elsewhere on the board
/LED+: D1.2 (A), J1.2
/LED-: D2.1 (K), J1.1
/Mag0_A: J8.3; also elsewhere on the board
/Mag0_B: J8.4; also elsewhere on the board
/Mag1_A: J9.3; also elsewhere on the board
/Mag1_B: J9.4; also elsewhere on the board
/Mag2_A: J10.3; also elsewhere on the board
/Mag2_B: J10.4; also elsewhere on the board
/Sensor0_Cs: J5.3; also elsewhere on the board
/Sensor0_Motion: J5.4; also elsewhere on the board
/Sensor0_Sck: J5.6; also elsewhere on the board
/Sensor0_Sdio: J5.5; also elsewhere on the board
/Sensor1_Cs: J6.3; also elsewhere on the board
/Sensor1_Motion: J6.4; also elsewhere on the board
/Sensor1_Sck: J6.6; also elsewhere on the board
/Sensor1_Sdio: J6.5; also elsewhere on the board
/Sensor2_Cs: J7.3; also elsewhere on the board
/Sensor2_Motion: J7.4; also elsewhere on the board
/Sensor2_Sck: J7.6; also elsewhere on the board
/Sensor2_Sdio: J7.5; also elsewhere on the board
GND: C1.2, C2.2, C12.2, C13.2, J2.2, J5.2, J6.2, J7.2, J8.2, J9.2, J10.2, U1.2 (GND), U3.2 (GND); also elsewhere on the board
unnamed: C1.1, R1.1, U1.1 (IN), U1.3 (EN)
unnamed: C12.1, R7.1, U3.1 (IN), U3.3 (EN)
unnamed: D1.1 (K), D3.2 (A)
unnamed: D2.2 (A), D3.1 (K)

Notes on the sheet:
VCC / GND not connected to avoid loop
Second 3.3V rail (3V3) for Sensor0, Sensor2
Separate supply rail +3V3 for Sensor0, Sensor2

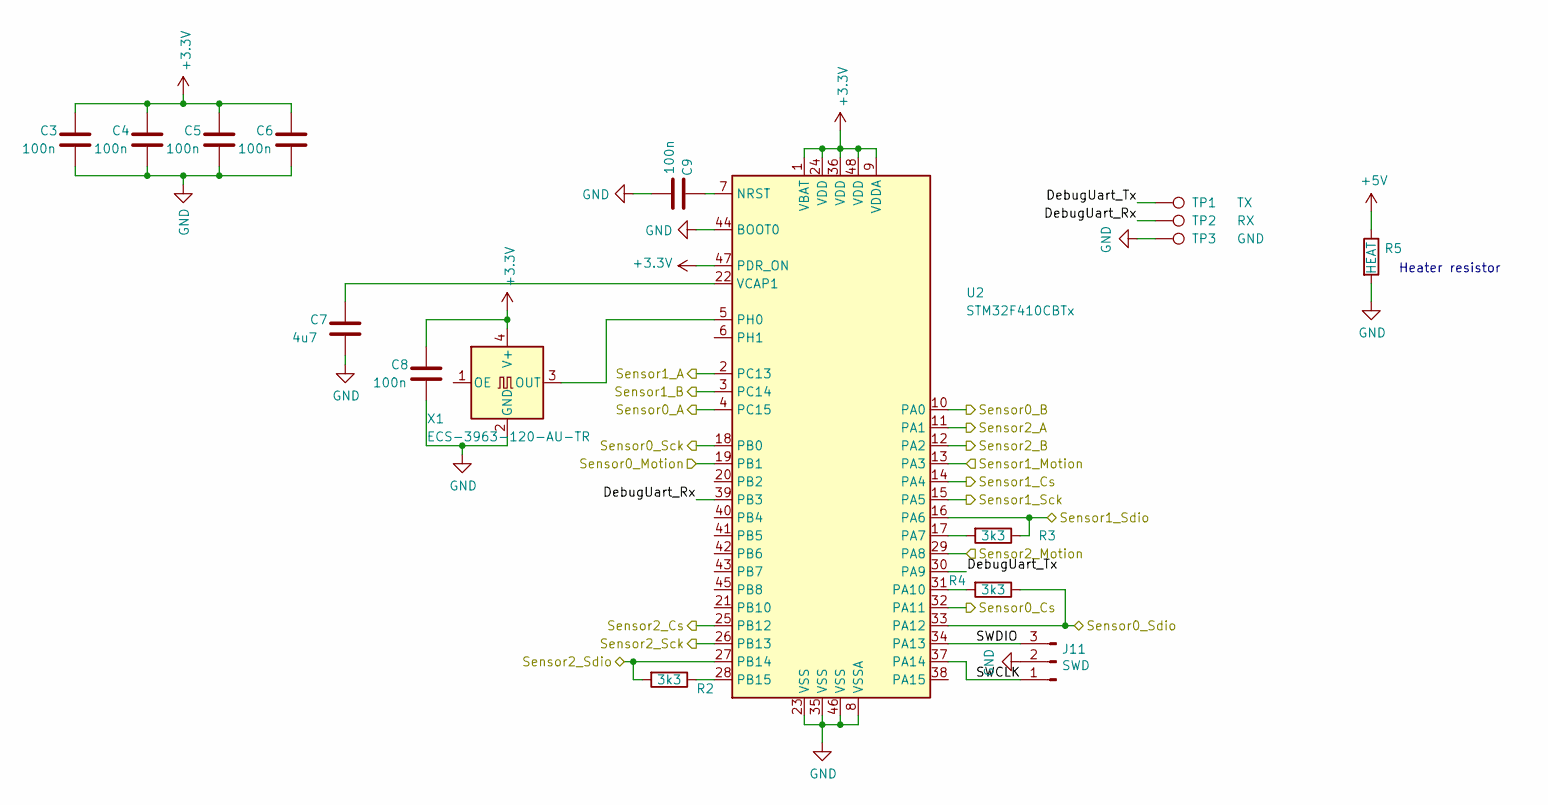
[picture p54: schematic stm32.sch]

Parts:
C3, C4, C5, C6, C8, C9: 100n; C_0603_1608Metric
C7: 4u7; C_0805_2012Metric
J11: SWD; PinHeader_1x03_P2.54mm_Vertical
R2, R3, R4: 3k3; R_0603_1608Metric
R5: HEAT; R_0805_2012Metric
TP1: TX; TestPoint_THTPad_D1.5mm_Drill0.7mm
TP2: RX; TestPoint_THTPad_D1.5mm_Drill0.7mm
TP3: GND; TestPoint_THTPad_D1.5mm_Drill0.7mm
U2: STM32F410CBTx; LQFP-48_7x7mm_P0.5mm
X1: ECS-3963-120-AU-TR; Oscillator_SMD_SeikoEpson_SG8002LB-4Pin_5.0x3.2mm

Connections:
+3V3: C3.1, C4.1, C5.1, C6.1, C8.1, U2.1 (VBAT), U2.9 (VDDA), U2.24 (VDD), U2.36 (VDD), U2.47 (PDR_ON), U2.48 (VDD), X1.4 (V+); also elsewhere on the board
+5V: R5.1; also elsewhere on the board
/STM32/DebugUart_Rx: TP2.1, U2.39 (PB3)
/STM32/DebugUart_Tx: TP1.1, U2.30 (PA9)
/STM32/SWCLK: J11.1, U2.37 (PA14)
/STM32/SWDIO: J11.3, U2.34 (PA13)
/Sensor0_Cs: U2.32 (PA11); also elsewhere on the board
/Sensor0_Motion: U2.19 (PB1); also elsewhere on the board
/Sensor0_Sck: U2.18 (PB0); also elsewhere on the board
/Sensor0_Sdio: R4.1, U2.33 (PA12); also elsewhere on the board
/Sensor1_Cs: U2.14 (PA4); also elsewhere on the board
/Sensor1_Motion: U2.13 (PA3); also elsewhere on the board
/Sensor1_Sck: U2.15 (PA5); also elsewhere on the board
/Sensor1_Sdio: R3.1, U2.16 (PA6); also elsewhere on the board
/Sensor2_Cs: U2.25 (PB12); also elsewhere on the board
/Sensor2_Motion: U2.29 (PA8); also elsewhere on the board
/Sensor2_Sck: U2.26 (PB13); also elsewhere on the board
/Sensor2_Sdio: R2.2, U2.27 (PB14); also elsewhere on the board
/Sensor_Selection/Optical0_A: U2.4 (PC15); also elsewhere on the board
/Sensor_Selection/Optical0_B: U2.10 (PA0); also elsewhere on the board
/Sensor_Selection/Optical1_A: U2.2 (PC13); also elsewhere on the board
/Sensor_Selection/Optical1_B: U2.3 (PC14); also elsewhere on the board
/Sensor_Selection/Optical2_A: U2.11 (PA1); also elsewhere on the board
/Sensor_Selection/Optical2_B: U2.12 (PA2); also elsewhere on the board
GND: C3.2, C4.2, C5.2, C6.2, C7.2, C8.2, C9.2, J11.2, R5.2, TP3.1, U2.8 (VSSA), U2.23 (VSS), U2.35 (VSS), U2.44 (BOOT0), U2.46 (VSS), X1.2 (GND); also elsewhere on the board
unnamed: C7.1, U2.22 (VCAP1)
unnamed: C9.1, U2.7 (NRST)
unnamed: R2.1, U2.28 (PB15)
unnamed: R3.2, U2.17 (PA7)
unnamed: R4.2, U2.31 (PA10)
unnamed: U2.5 (PH0), X1.3 (OUT)

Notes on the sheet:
Heater resistor

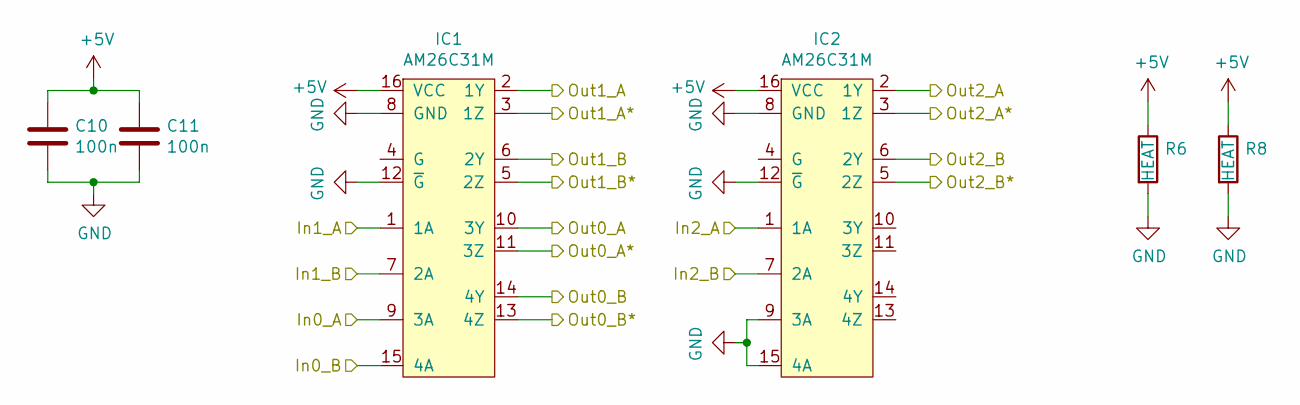
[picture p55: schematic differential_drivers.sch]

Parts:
C10, C11: 100n; C_0603_1608Metric
IC1, IC2: AM26C31M; SOIC-16_3.9x9.9mm_P1.27mm; Farnell 4975637
R6, R8: HEAT; R_0805_2012Metric

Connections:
+5V: C10.1, C11.1, IC1.16 (VCC), IC2.16 (VCC), R6.1, R8.1; also elsewhere on the board
/Differential_Drivers/In0_A: IC1.9 (3A); also elsewhere on the board
/Differential_Drivers/In0_B: IC1.15 (4A); also elsewhere on the board
/Differential_Drivers/In1_A: IC1.1 (1A); also elsewhere on the board
/Differential_Drivers/In1_B: IC1.7 (2A); also elsewhere on the board
/Differential_Drivers/In2_A: IC2.1 (1A); also elsewhere on the board
/Differential_Drivers/In2_B: IC2.7 (2A); also elsewhere on the board
/Differential_Drivers/Out0_A: IC1.10 (3Y); also elsewhere on the board
/Differential_Drivers/Out0_A*: IC1.11 (3Z); also elsewhere on the board
/Differential_Drivers/Out0_B: IC1.14 (4Y); also elsewhere on the board
/Differential_Drivers/Out0_B*: IC1.13 (4Z); also elsewhere on the board
/Differential_Drivers/Out1_A: IC1.2 (1Y); also elsewhere on the board
/Differential_Drivers/Out1_A*: IC1.3 (1Z); also elsewhere on the board
/Differential_Drivers/Out1_B: IC1.6 (2Y); also elsewhere on the board
/Differential_Drivers/Out1_B*: IC1.5 (2Z); also elsewhere on the board
/Differential_Drivers/Out2_A: IC2.2 (1Y); also elsewhere on the board
/Differential_Drivers/Out2_A*: IC2.3 (1Z); also elsewhere on the board
/Differential_Drivers/Out2_B: IC2.6 (2Y); also elsewhere on the board
/Differential_Drivers/Out2_B*: IC2.5 (2Z); also elsewhere on the board
GND: C10.2, C11.2, IC1.8 (GND), IC1.12 (~G), IC2.8 (GND), IC2.9 (3A), IC2.12 (~G), IC2.15 (4A), R6.2, R8.2; also elsewhere on the board

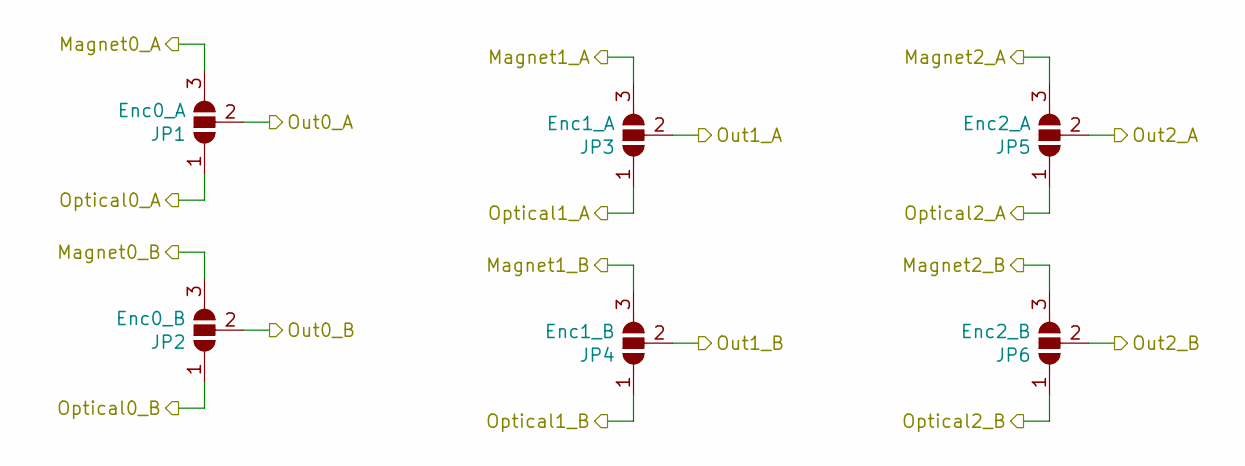
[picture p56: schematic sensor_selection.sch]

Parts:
JP1: Enc0_A; SolderJumper-3_P1.3mm_Open_RoundedPad1.0x1.5mm
JP2: Enc0_B; SolderJumper-3_P1.3mm_Open_RoundedPad1.0x1.5mm
JP3: Enc1_A; SolderJumper-3_P1.3mm_Open_RoundedPad1.0x1.5mm
JP4: Enc1_B; SolderJumper-3_P1.3mm_Open_RoundedPad1.0x1.5mm
JP5: Enc2_A; SolderJumper-3_P1.3mm_Open_RoundedPad1.0x1.5mm
JP6: Enc2_B; SolderJumper-3_P1.3mm_Open_RoundedPad1.0x1.5mm

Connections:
/Differential_Drivers/In0_A: JP1.2 (C); also elsewhere on the board
/Differential_Drivers/In0_B: JP2.2 (C); also elsewhere on the board
/Differential_Drivers/In1_A: JP3.2 (C); also elsewhere on the board
/Differential_Drivers/In1_B: JP4.2 (C); also elsewhere on the board
/Differential_Drivers/In2_A: JP5.2 (C); also elsewhere on the board
/Differential_Drivers/In2_B: JP6.2 (C); also elsewhere on the board
/Mag0_A: JP1.3 (B); also elsewhere on the board
/Mag0_B: JP2.3 (B); also elsewhere on the board
/Mag1_A: JP3.3 (B); also elsewhere on the board
/Mag1_B: JP4.3 (B); also elsewhere on the board
/Mag2_A: JP5.3 (B); also elsewhere on the board
/Mag2_B: JP6.3 (B); also elsewhere on the board
/Sensor_Selection/Optical0_A: JP1.1 (A); also elsewhere on the board
/Sensor_Selection/Optical0_B: JP2.1 (A); also elsewhere on the board
/Sensor_Selection/Optical1_A: JP3.1 (A); also elsewhere on the board
/Sensor_Selection/Optical1_B: JP4.1 (A); also elsewhere on the board
/Sensor_Selection/Optical2_A: JP5.1 (A); also elsewhere on the board
/Sensor_Selection/Optical2_B: JP6.1 (A); also elsewhere on the board



Board: 2 copper layers, 148.5 x 148.9 mm, 60 parts (3 on the bottom side), 62 nets.

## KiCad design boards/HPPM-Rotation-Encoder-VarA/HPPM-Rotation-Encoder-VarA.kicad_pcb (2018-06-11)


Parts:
C1, C3: 100n; C_0603
C2: 4µ7 6V3; C_0603
C4: 1µ 10V; C_0603
D1: Yellow; LED_0603
D2: Red; LED_0603
J1: CONN; Pin_Header_Straight_1x06_Pitch2.54mm
R1, R2: 2k; R_0603
R3, R4: HEAT; R_1206
U1: AS5045B; SSOP-16_5.3x6.2mm_Pitch0.65mm
U2: DS9638; SOIC-8_3.9x4.9mm_Pitch1.27mm

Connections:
+5V: C1.1, C3.1, C4.1, J1.1, R1.2, R2.2, R3.1, R4.1, U1.16 (VDD5V), U2.1 (VCC)
/A: J1.3, U2.8 (OUT_A)
/A*: J1.4, U2.7 (OUT_A*)
/B: J1.5, U2.6 (OUT_B)
/B*: J1.6, U2.5 (OUT_B*)
/_A: U1.3 (A), U2.2 (IN_A)
/_B: U1.4 (B), U2.3 (IN_B)
GND: C1.2, C2.2, C3.2, C4.2, J1.2, R3.2, R4.2, U1.7 (VSS), U1.8 (PDIO), U1.10 (CLK), U2.4 (GND)
unnamed: C2.1, U1.15 (VDD3V3)
unnamed: D1.1 (K), U1.1 (~MagINC)
unnamed: D1.2 (A), R1.1
unnamed: D2.1 (K), U1.2 (~MagDEC)
unnamed: D2.2 (A), R2.1

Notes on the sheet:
I_LED = 1..2mA



Board: 2 copper layers, 15.0 x 31.2 mm, 13 parts (3 on the bottom side), 13 nets.

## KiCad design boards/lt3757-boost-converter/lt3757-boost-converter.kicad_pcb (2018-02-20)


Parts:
J1, J9: GND; MountingHole_3.2mm_M3_Pad
J2: Enable; Measurement_Point_Round-SMD-Pad_Small
J3: BAT; MountingHole_3.2mm_M3_Pad
J4: 24V; MountingHole_3.2mm_M3_Pad
J5, J6, J7, J8: M3; MountingHole_3.2mm_M3

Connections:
/LT3757/24V_OUT: J4.1; also elsewhere on the board
/LT3757/Bat_IN: J3.1; also elsewhere on the board
/LT3757/Enable: J2.1; also elsewhere on the board
GND: J1.1, J9.1; also elsewhere on the board

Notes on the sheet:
Mounting holes


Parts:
C1, C2, C3, C4, C5: 120µ; CP_Elec_10x10.5
C6, C15, C16, C17: 100n; C_0603_HandSoldering
C7: (2n2); C_0603_HandSoldering
C8: 100p; C_0603_HandSoldering
C9: 4µ7; C_0805_HandSoldering
C10: 6n8; C_0603_HandSoldering
C11: (470p); C_0603_HandSoldering
C12: 10µ; C_0603_HandSoldering
C13, C14: 1µ; C_0603_HandSoldering
D1: VS-42CTQ030S-M3; TO-263-3Lead
L1: 2.4µH; Inductor_Wurth_HCI-1890
Q1: FDB86566; TO-263-3Lead
R1: 100k; R_0603_HandSoldering
R2: 27k; R_0603_HandSoldering
R3: 150k; R_0603_HandSoldering
R4: (22); R_0603_HandSoldering
R5: 10k5; R_0603_HandSoldering
R6: 2m; WSLP2726
R7: 13k; R_0603_HandSoldering
R8: 22k; R_0603_HandSoldering
TP1, TP2: FBX; Measurement_Point_Round-SMD-Pad_Small
U1: LT3757; MSOP-10-1EP_3x3mm_Pitch0.5mm

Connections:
/LT3757/24V_OUT: C2.1, C3.1, C4.1, C5.1, C12.1, C13.1, C14.1, C15.1, C16.1, D1.2 (K), TP2.1; also elsewhere on the board
/LT3757/Bat_IN: C1.1, C9.1, C17.1, L1.1, R1.1, U1.8 (INTVcc), U1.10 (Vin); also elsewhere on the board
/LT3757/Enable: R1.2, R2.1, U1.9 (~SHDN~/UVLO); also elsewhere on the board
/LT3757/FBX: C11.1, R3.2, R7.1, U1.2 (FBX)
/LT3757/GATE: Q1.1 (G), U1.7 (GATE)
/LT3757/L_D_FET: D1.1 (A), D1.3 (A), L1.2, Q1.2 (D)
/LT3757/RT: R5.1, U1.4 (RT)
/LT3757/SS: C6.1, U1.3 (SS)
/LT3757/V_SENSE: C7.1, R4.2, U1.6 (SENSE)
/LT3757/V_c: C8.1, R8.1, U1.1 (Vc)
GND: C1.2, C2.2, C3.2, C4.2, C5.2, C6.2, C7.2, C8.2, C9.2, C10.2, C11.2, C12.2, C13.2, C14.2, C15.2, C16.2, C17.2, R2.2, R5.2, R6.1, R7.2, U1.5 (SYNC), U1.11 (GND); also elsewhere on the board
unnamed: C10.1, R8.2
unnamed: Q1.3 (S), R4.1, R6.2
unnamed: R3.1, TP1.1

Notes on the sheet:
Würth 7443556260 L=2.4µH I_R=31.5A I_SAT=50A R_DC=1.58mOhm L_R=2.15µH
Vishay VS-42CTQ030S-M3 30V 2x20A D²PAK (TO-263AB) V_F=0.38V
Capacitors: 1x + 4x Panasonic 35SVPF82M 35V 82µF 20mΩ, I_ripple=4A Mouser #667-35SVPF82M
Vishay WSLP2726 2mΩ
Fairchild FDB86566 60V 110A 2.7mΩ G_Q=80nC C_RSS=57pF
Old: Würth 7443556082 Old: L=0.82µH I_R=41.5A I_SAT=65A R_DC=0.54mOhm L_R=0.72µH
manual copper wire
V_out = 1.6V * (1+ R1/R2) = 1.6V * (1 + (150k/13k)) = 20.06V


Board: 2 copper layers, 44.2 x 64.8 mm, 40 parts (0 on the bottom side), 14 nets.

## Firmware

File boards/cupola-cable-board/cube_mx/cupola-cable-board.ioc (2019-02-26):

#MicroXplorer Configuration settings - do not modify
File.Version=6
KeepUserPlacement=false
Mcu.Family=STM32F4
Mcu.IP0=NVIC
Mcu.IP1=RCC
Mcu.IP2=SPI1
Mcu.IP3=SPI2
Mcu.IP4=SPI5
Mcu.IP5=SYS
Mcu.IP6=USART1
Mcu.IPNb=7
Mcu.Name=STM32F410C(8-B)Tx
Mcu.Package=LQFP48
Mcu.Pin0=PC13-ANTI_TAMP
Mcu.Pin1=PC14-OSC32_IN
Mcu.Pin10=PA5
Mcu.Pin11=PA6
Mcu.Pin12=PA7
Mcu.Pin13=PB0
Mcu.Pin14=PB1
Mcu.Pin15=PB12
Mcu.Pin16=PB13
Mcu.Pin17=PB14
Mcu.Pin18=PB15
Mcu.Pin19=PA8
Mcu.Pin2=PC15-OSC32_OUT
Mcu.Pin20=PA9
Mcu.Pin21=PA10
Mcu.Pin22=PA11
Mcu.Pin23=PA12
Mcu.Pin24=PA13
Mcu.Pin25=PA14
Mcu.Pin26=PB3
Mcu.Pin27=VP_SYS_VS_Systick
Mcu.Pin3=PH0 - OSC_IN
Mcu.Pin4=PH1 - OSC_OUT
Mcu.Pin5=PA0-WKUP
Mcu.Pin6=PA1
Mcu.Pin7=PA2
Mcu.Pin8=PA3
Mcu.Pin9=PA4
Mcu.PinsNb=28
Mcu.ThirdPartyNb=0
Mcu.UserConstants=
Mcu.UserName=STM32F410CBTx
MxCube.Version=4.26.1
MxDb.Version=DB.4.0.261
NVIC.BusFault_IRQn=true\:0\:0\:false\:false\:true\:false
NVIC.DebugMonitor_IRQn=true\:0\:0\:false\:false\:true\:false
NVIC.HardFault_IRQn=true\:0\:0\:false\:false\:true\:false
NVIC.MemoryManagement_IRQn=true\:0\:0\:false\:false\:true\:false
NVIC.NonMaskableInt_IRQn=true\:0\:0\:false\:false\:true\:false
NVIC.PendSV_IRQn=true\:0\:0\:false\:false\:true\:false
NVIC.PriorityGroup=NVIC_PRIORITYGROUP_4
NVIC.SVCall_IRQn=true\:0\:0\:false\:false\:true\:false
NVIC.SysTick_IRQn=true\:0\:0\:false\:false\:true\:false
NVIC.UsageFault_IRQn=true\:0\:0\:false\:false\:true\:false
PA0-WKUP.GPIOParameters=GPIO_Label
PA0-WKUP.GPIO_Label=Sensor0_B
PA0-WKUP.Locked=true
PA0-WKUP.Signal=GPIO_Output
PA1.GPIOParameters=GPIO_Label
PA1.GPIO_Label=Sensor2_A
PA1.Locked=true
PA1.Signal=GPIO_Output
PA10.Locked=true
PA10.Mode=Full_Duplex_Master
PA10.Signal=SPI5_MOSI
PA11.GPIOParameters=GPIO_Label
PA11.GPIO_Label=Sensor0_Cs
PA11.Locked=true
PA11.Signal=GPIO_Output
PA12.Locked=true
PA12.Mode=Full_Duplex_Master
PA12.Signal=SPI5_MISO
PA13.Mode=Serial_Wire
PA13.Signal=SYS_JTMS-SWDIO
PA14.Mode=Serial_Wire
PA14.Signal=SYS_JTCK-SWCLK
PA2.GPIOParameters=GPIO_Label
PA2.GPIO_Label=Sensor2_B
PA2.Locked=true
PA2.Signal=GPIO_Output
PA3.GPIOParameters=GPIO_Label
PA3.GPIO_Label=Sensor1_Motion
PA3.Locked=true
PA3.Signal=GPIO_Input
PA4.GPIOParameters=GPIO_Label
PA4.GPIO_Label=Sensor1_Cs
PA4.Locked=true
PA4.Signal=GPIO_Output
PA5.Locked=true
PA5.Mode=Full_Duplex_Master
PA5.Signal=SPI1_SCK
PA6.Locked=true
PA6.Mode=Full_Duplex_Master
PA6.Signal=SPI1_MISO
PA7.Locked=true
PA7.Mode=Full_Duplex_Master
PA7.Signal=SPI1_MOSI
PA8.GPIOParameters=GPIO_Label
PA8.GPIO_Label=Sensor2_Motion
PA8.Locked=true
PA8.Signal=GPIO_Input
PA9.Locked=true
PA9.Mode=Asynchronous
PA9.Signal=USART1_TX
PB0.Mode=Full_Duplex_Master
PB0.Signal=SPI5_SCK
PB1.GPIOParameters=GPIO_Label
PB1.GPIO_Label=Sensor0_Motion
PB1.Locked=true
PB1.Signal=GPIO_Input
PB12.GPIOParameters=GPIO_Label
PB12.GPIO_Label=Sensor2_Cs
PB12.Locked=true
PB12.Signal=GPIO_Output
PB13.Locked=true
PB13.Mode=Full_Duplex_Master
PB13.Signal=SPI2_SCK
PB14.Locked=true
PB14.Mode=Full_Duplex_Master
PB14.Signal=SPI2_MISO
PB15.Locked=true
PB15.Mode=Full_Duplex_Master
PB15.Signal=SPI2_MOSI
PB3.Locked=true
PB3.Mode=Asynchronous
PB3.Signal=USART1_RX
PC13-ANTI_TAMP.GPIOParameters=GPIO_Label
PC13-ANTI_TAMP.GPIO_Label=Sensor1_A
PC13-ANTI_TAMP.Locked=true
PC13-ANTI_TAMP.Signal=GPIO_Output
PC14-OSC32_IN.GPIOParameters=GPIO_Label
PC14-OSC32_IN.GPIO_Label=Sensor1_B
PC14-OSC32_IN.Locked=true
PC14-OSC32_IN.Signal=GPIO_Output
PC15-OSC32_OUT.GPIOParameters=GPIO_Label
PC15-OSC32_OUT.GPIO_Label=Sensor0_A
PC15-OSC32_OUT.Locked=true
PC15-OSC32_OUT.Signal=GPIO_Output
PCC.Checker=false
PCC.Line=STM32F410
PCC.MCU=STM32F410C(8-B)Tx
PCC.PartNumber=STM32F410CBTx
PCC.Seq0=0
PCC.Series=STM32F4
PCC.Temperature=25
PCC.Vdd=null
PH0\ -\ OSC_IN.Locked=true
PH0\ -\ OSC_IN.Mode=HSE-External-Oscillator
PH0\ -\ OSC_IN.Signal=RCC_OSC_IN
PH1\ -\ OSC_OUT.Mode=HSE-External-Oscillator
PH1\ -\ OSC_OUT.Signal=RCC_OSC_OUT
PinOutPanel.RotationAngle=0
RCC.48MHZClocksFreq_Value=25000000
RCC.AHBFreq_Value=50000000
RCC.APB1CLKDivider=RCC_HCLK_DIV2
RCC.APB1Freq_Value=25000000
RCC.APB1TimFreq_Value=50000000
RCC.APB2Freq_Value=50000000
RCC.APB2TimFreq_Value=50000000
RCC.CortexFreq_Value=50000000
RCC.EthernetFreq_Value=50000000
RCC.FCLKCortexFreq_Value=50000000
RCC.FMPI2C1Freq_Value=25000000
RCC.FamilyName=M
RCC.HCLKFreq_Value=50000000
RCC.HSE_VALUE=12000000
RCC.HSI_VALUE=16000000
RCC.I2SClocksFreq_Value=50000000
RCC.IPParameters=48MHZClocksFreq_Value,AHBFreq_Value,APB1CLKDivider,APB1Freq_Value,APB1TimFreq_Value,APB2Freq_Value,APB2TimFreq_Value,CortexFreq_Value,EthernetFreq_Value,FCLKCortexFreq_Value,FMPI2C1Freq_Value,FamilyName,HCLKFreq_Value,HSE_VALUE,HSI_VALUE,I2SClocksFreq_Value,LPTIM1Freq_Value,LSE_VALUE,LSI_VALUE,PLLCLKFreq_Value,PLLM,PLLN,PLLSourceVirtual,RTCFreq_Value,RTCHSEDivFreq_Value,SYSCLKFreq_VALUE,SYSCLKSource,VCOInputFreq_Value,VCOOutputFreq_Value,VCOQOutputFreq_Value,VCOROutputFreq_Value
RCC.LPTIM1Freq_Value=25000000
RCC.LSE_VALUE=32768
RCC.LSI_VALUE=32000
RCC.PLLCLKFreq_Value=50000000
RCC.PLLM=12
RCC.PLLN=100
RCC.PLLSourceVirtual=RCC_PLLSOURCE_HSE
RCC.RTCFreq_Value=32000
RCC.RTCHSEDivFreq_Value=6000000
RCC.SYSCLKFreq_VALUE=50000000
RCC.SYSCLKSource=RCC_SYSCLKSOURCE_PLLCLK
RCC.VCOInputFreq_Value=1000000
RCC.VCOOutputFreq_Value=100000000
RCC.VCOQOutputFreq_Value=25000000
RCC.VCOROutputFreq_Value=50000000
SPI1.CalculateBaudRate=25.0 MBits/s
SPI1.Direction=SPI_DIRECTION_2LINES
SPI1.IPParameters=VirtualType,Mode,Direction,CalculateBaudRate
SPI1.Mode=SPI_MODE_MASTER
SPI1.VirtualType=VM_MASTER
SPI2.BaudRatePrescaler=SPI_BAUDRATEPRESCALER_2
SPI2.CalculateBaudRate=12.5 MBits/s
SPI2.Direction=SPI_DIRECTION_2LINES
SPI2.IPParameters=VirtualType,Mode,Direction,CalculateBaudRate,BaudRatePrescaler
SPI2.Mode=SPI_MODE_MASTER
SPI2.VirtualType=VM_MASTER
SPI5.CalculateBaudRate=25.0 MBits/s
SPI5.Direction=SPI_DIRECTION_2LINES
SPI5.IPParameters=VirtualType,Mode,Direction,CalculateBaudRate
SPI5.Mode=SPI_MODE_MASTER
SPI5.VirtualType=VM_MASTER
USART1.IPParameters=VirtualMode
USART1.VirtualMode=VM_ASYNC
VP_SYS_VS_Systick.Mode=SysTick
VP_SYS_VS_Systick.Signal=SYS_VS_Systick
board=custom

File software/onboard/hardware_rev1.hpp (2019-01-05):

/* hardware_rev1.hpp
 *
 * Copyright (C) 2017 Raphael Lehmann <raphael@rleh.de>
 *
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
 * You should have received a copy of the GNU General Public License
 * along with this program.  If not, see <http://www.gnu.org/licenses/>.
 */

#ifndef HARDWARE_REV1_HPP
#define HARDWARE_REV1_HPP

#include <xpcc/architecture/platform.hpp>

#include <xpcc/io/iostream.hpp>

using namespace xpcc::stm32;

namespace Board
{

/// STM32F429 running at 180MHz from the external 8MHz crystal
struct systemClock
{
	static constexpr uint32_t Frequency = MHz180;
	static constexpr uint32_t Apb1 = Frequency / 4;
	static constexpr uint32_t Apb2 = Frequency / 2;

	static constexpr uint32_t Adc = Apb2;

	static constexpr uint32_t Spi1 = Apb2;
	static constexpr uint32_t Spi2 = Apb1;
	static constexpr uint32_t Spi3 = Apb1;
	static constexpr uint32_t Spi4 = Apb2;
	static constexpr uint32_t Spi5 = Apb2;
	static constexpr uint32_t Spi6 = Apb2;

	static constexpr uint32_t Usart1 = Apb2;
	static constexpr uint32_t Usart2 = Apb1;
	static constexpr uint32_t Usart3 = Apb1;
	static constexpr uint32_t Uart4  = Apb1;
	static constexpr uint32_t Uart5  = Apb1;
	static constexpr uint32_t Usart6 = Apb2;
	static constexpr uint32_t Uart7  = Apb1;
	static constexpr uint32_t Uart8  = Apb1;

	static constexpr uint32_t Can1 = Apb1;
	static constexpr uint32_t Can2 = Apb1;

	static constexpr uint32_t I2c1 = Apb1;
	static constexpr uint32_t I2c2 = Apb1;
	static constexpr uint32_t I2c3 = Apb1;
	static constexpr uint32_t I2c4 = Apb1;

	static constexpr uint32_t Apb1Timer = Apb1 * 2;
	static constexpr uint32_t Apb2Timer = Apb2 * 2;
	static constexpr uint32_t Timer1  = Apb2Timer;
	static constexpr uint32_t Timer2  = Apb1Timer;
	static constexpr uint32_t Timer3  = Apb1Timer;
	static constexpr uint32_t Timer4  = Apb1Timer;
	static constexpr uint32_t Timer5  = Apb1Timer;
	static constexpr uint32_t Timer6  = Apb1Timer;
	static constexpr uint32_t Timer7  = Apb1Timer;
	static constexpr uint32_t Timer8  = Apb2Timer;
	static constexpr uint32_t Timer9  = Apb2Timer;
	static constexpr uint32_t Timer10 = Apb2Timer;
	static constexpr uint32_t Timer11 = Apb2Timer;
	static constexpr uint32_t Timer12 = Apb1Timer;
	static constexpr uint32_t Timer13 = Apb1Timer;
	static constexpr uint32_t Timer14 = Apb1Timer;

	static bool inline
	enable()
	{
		ClockControl::enableExternalCrystal(); // 8 MHz
		ClockControl::enablePll(
			ClockControl::PllSource::ExternalCrystal,
			4,      // 8MHz / N=4 -> 2MHz
			180,    // 2MHz * M=180 -> 360MHz
			2,      // 360MHz / P=2 -> 180MHz = F_cpu
			7       // 360MHz / Q=7 -> ~51MHz = F_usb => bad for USB
		);
		/*ClockControl::enableInternalClock(); // 16 MHz
		ClockControl::enablePll(
			ClockControl::PllSource::InternalClock,
			8,      // 16MHz / N=8 -> 2MHz
			180,    // 2MHz * M=180 -> 360MHz
			2,      // 360MHz / P=2 -> 180MHz = F_cpu
			7       // 360MHz / Q=7 -> ~51MHz = F_usb => bad for USB
		);*/

		// Enable overdrive mode
		PWR->CR |= PWR_CR_ODEN;
		// wait for it
		while (not (PWR->CSR & PWR_CSR_ODRDY)) ;
		ClockControl::setFlashLatency(Frequency);
		ClockControl::enableSystemClock(ClockControl::SystemClockSource::Pll);
		ClockControl::setApb1Prescaler(ClockControl::Apb1Prescaler::Div4);
		ClockControl::setApb2Prescaler(ClockControl::Apb2Prescaler::Div2);
		// update clock frequencies
		xpcc::clock::fcpu     = Frequency;
		xpcc::clock::fcpu_kHz = Frequency / 1000;
		xpcc::clock::fcpu_MHz = Frequency / 1000000;
		xpcc::clock::ns_per_loop = ::round(3000 / (Frequency / 1000000));

		return true;
	}
};


template<typename SpiStruct, uint32_t SpiBaudrate>
inline void
spiMasterInitialize()
{
	SpiStruct::Sck::connect(SpiStruct::Spi::Sck);
	SpiStruct::Mosi::connect(SpiStruct::Spi::Mosi);
	SpiStruct::Miso::connect(SpiStruct::Spi::Miso);
	SpiStruct::Spi::template initialize<systemClock, SpiBaudrate>();
}

template <typename Timer, typename Pin, uint32_t Prescaler, uint32_t Overflow>
inline void
TimerPwmCh1Initialize() {
	Timer::enable();
	Timer::setMode(Timer::Mode::UpCounter,
	                Timer::SlaveMode::Disabled,
	                Timer::SlaveModeTrigger::Internal0,
	                Timer::MasterMode::CompareOc1Ref);

	Timer::setPrescaler(Prescaler);
	Timer::setOverflow(Overflow);

	Timer::forceInactive(1);
	Timer::configureOutputChannel(1, Timer::OutputCompareMode::Pwm, 0);
	Timer::forceInactive(1);

	Timer::applyAndReset();
	Timer::pause();
	Pin::connect(Timer::Channel1);
}

namespace Ui {
	using LedRed		= GpioOutputG3;	// LED1
	using LedGreen		= GpioOutputG4;	// LED2
	using LedBlue		= GpioOutputG5;	// LED3

	using Button1		= GpioInputG13;	// SW1
	using Button2		= GpioInputG14;	// SW1

	//using DebugUartRx	= GpioInputA10;
	using DebugUartRx	= GpioOutputA10;
	using DebugUartTx	= GpioOutputA9;
	using DebugUart		= Usart1;
	constexpr uint32_t DebugBaudrate = DebugUart::Baudrate::B115200;

	inline void
	initialize()
	{
		LedRed::setOutput(xpcc::Gpio::High);
		LedGreen::setOutput(xpcc::Gpio::High);
		LedBlue::setOutput(xpcc::Gpio::High);

		Button1::setInput(Gpio::InputType::PullUp);
		Button2::setInput(Gpio::InputType::PullUp);

		//DebugUartRx::connect(DebugUart::Rx);
		//DebugUartTx::connect(DebugUart::Tx);
		DebugUartTx::setOutput(false);
		DebugUartRx::setOutput(false);
		DebugUart::initialize<systemClock, DebugBaudrate>(12);
	}
}

namespace Camera {
	//constexpr uint16_t PwmPeriod		= 100;
	// PWM frequency 10kHz (period 100us)

	using LightPin		= GpioOutputB14;
	using LensHeatPin	= GpioOutputB15;

	//using CameraTimer	= Timer12;

	using PiUart	= Uart8;
	using PiUartRx	= GpioE0;
	using PiUartTx	= GpioE1;
	constexpr uint32_t PiBaudrate = PiUart::Baudrate::B115200;

	inline void
	initialize() {
		//CameraTimer::enable();
		//CameraTimer::setMode(CameraTimer::Mode::UpCounter,
		//                     CameraTimer::SlaveMode::Disabled,
		//                     CameraTimer::SlaveModeTrigger::Internal0,
		//                     CameraTimer::MasterMode::CompareOc1Ref);
		//CameraTimer::setPeriod<systemClock>(PwmPeriod, false);
		//CameraTimer::forceInactive(1);
		//CameraTimer::forceInactive(2);
		//CameraTimer::configureOutputChannel(1, CameraTimer::OutputCompareMode::Pwm2, 0x7FFF, CameraTimer::PinState::Disable);
		//CameraTimer::configureOutputChannel(2, CameraTimer::OutputCompareMode::Pwm2, 0x7FFF, CameraTimer::PinState::Disable);
		//CameraTimer::applyAndReset();
		//CameraTimer::pause();
		//LightPin::connect(CameraTimer::Channel1);
		//LensHeatPin::connect(CameraTimer::Channel2);
		LightPin::setOutput();

		PiUartRx::connect(PiUart::Rx);
		PiUartTx::connect(PiUart::Tx);
		PiUart::initialize<systemClock, PiBaudrate>(12);
	}
}

namespace Rxsm {
	using TelemetryRx		= GpioInputD2;
	using TelemetryTx		= GpioOutputC12;
	using TelemetryUart		= Uart5;
	constexpr uint32_t TelemetryBaudrate = TelemetryUart::Baudrate::B38400;

	using EventLo			= xpcc::GpioInverted<GpioInputD9>;
	using EventSoe			= xpcc::GpioInverted<GpioInputD10>;
	using EventSods			= xpcc::GpioInverted<GpioInputD11>;

	inline void
	initialize()
	{
		EventLo::setInput(Gpio::InputType::Floating);
		EventSoe::setInput(Gpio::InputType::Floating);
		EventSods::setInput(Gpio::InputType::Floating);

		TelemetryRx::connect(TelemetryUart::Rx);
		TelemetryTx::connect(TelemetryUart::Tx);
		TelemetryUart::initialize<systemClock, TelemetryBaudrate>(10);
	}
}
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

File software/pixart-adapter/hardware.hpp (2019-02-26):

/* hardware.hpp
 *
 * Copyright (C) 2019 Raphael Lehmann <raphael@rleh.de>
 *
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
 * You should have received a copy of the GNU General Public License
 * along with this program.  If not, see <http://www.gnu.org/licenses/>.
 */

#ifndef HARDWARE_HPP
#define HARDWARE_HPP

#include <modm/platform.hpp>
#include <modm/architecture/interface/clock.hpp>
#include <modm/platform/clock/clock.hpp>
#include <modm/platform/gpio/software_port.hpp>

using namespace modm::platform;

namespace Board
{

/// STM32F410 running at 50MHz generated with the PLL from 12MHz HSE oscillator

struct systemClock {
	static constexpr uint32_t Frequency = 50 * MHz1;
	static constexpr uint32_t Ahb = Frequency;
	static constexpr uint32_t Apb1 = Frequency / 2;
	static constexpr uint32_t Apb2 = Frequency;

	static constexpr uint32_t Usart1 = Apb2;
	static constexpr uint32_t Usart2 = Apb1;
	static constexpr uint32_t Usart6 = Apb2;

	static constexpr uint32_t Adc1 = Apb2;

	static constexpr uint32_t Dac = Apb1;

	static constexpr uint32_t Spi1 = Apb2;
	static constexpr uint32_t Spi2 = Apb1;
	static constexpr uint32_t Spi5 = Apb2;

	static constexpr uint32_t Timer1 = Apb2;
	static constexpr uint32_t Timer5 = Apb1;
	static constexpr uint32_t Timer6 = Apb1;
	static constexpr uint32_t Timer9 = Apb2;
	static constexpr uint32_t Timer11 = Apb2;


	static bool inline
	enable()
	{
		ClockControl::enableExternalClock();

		ClockControl::enablePll(
			ClockControl::PllSource::Hse,
			12,		// 12MHz / M=12 -> 1MHz
			100,	// 1MHz * N=100 -> 100MHz
			2		// 100MHz / P=2 -> 50MHz = F_cpu
		);
		ClockControl::setFlashLatency(Frequency);
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

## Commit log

2017-01-20 add ltc2984 board (draft)
    [ltc2984-board.kicad_pcb, ltc2984-board.sch]
2017-01-24 powerboard: initial schematic
    [powerboard.kicad_pcb, powerboard.sch, powerboard_motor_controller.sch, powerboard_regulator_28V-to-5V.sch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]
2017-01-24 powerboard: motor controller nSleep pullup voltage fixed
    [powerboard.sch, powerboard_motor_controller.sch, powerboard_regulator_28V-to-5V.sch, powerboard_stepup_24V_60W.sch]
2017-01-24 add mainboard (empty)
    [mainboard.kicad_pcb, mainboard.sch, mainboard_microcontroller.sch]
2017-01-24 powerboard: add heat probe current and voltage sensing
    [powerboard.sch, powerboard_motor_controller.sch, powerboard_regulator_28V-to-5V.sch, powerboard_stepup_24V_60W.sch]
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2017-01-26 add mainboard peripherie
    [mainboard.sch, mainboard_microcontroller.sch]
2017-01-26 mainboard: add STM32F429 MCU
    [mainboard.sch, mainboard_microcontroller.sch]
2017-01-26 mainboard: connect MCU to peripherals
    [mainboard.sch, mainboard_microcontroller.sch]
2017-01-26 powerboard: add lt1370 boost converter
    [powerboard.sch, powerboard_motor_controller.sch, powerboard_regulator_28V-to-5V.sch, powerboard_stepup_24V_60W.sch]
2017-01-26 powerboard: add LC filter to motor controller; rename signals
    [powerboard.sch, powerboard_motor_controller.sch]
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2017-01-30 ltc2984-board: layout: DRC passed and soldermask clearance
    [ltc2984-board.kicad_pcb]
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2017-02-19 lt3757-board: fix diode polarity in schematic and layout
    [lt3557-boost-converter.kicad_pcb, lt3757.sch]
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2017-03-09 fix lt3757 naming
    [lt3757-boost-converter.kicad_pcb, lt3757-boost-converter.sch, lt3757.sch]
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2017-03-14 mainboard: fix and improve various sections (see below)
    * add I2C pullups (pressure sensor)
    * power input: replace LC filter with PI-filter (f_g = ~15kHz)
    * RS-422: add common mode choke and ESD protection diodes
    * add opto-coupled RXSM event line inputs
    [mainboard.sch, mainboard_microcontroller.sch]
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2017-04-14 [mainboard] various fixes
    * remove force sensors interface and ADC
    * add linear position sensor interface
    * pressure sensor voltage
    * remove 1-wire temperature sensor interface
    * add I2C temperature sensor interface
    * remove control panel
    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
    [mainboard.sch, mainboard_microcontroller.sch]
2017-04-14 [mainboard] various fixes to ADC and connectors
    * remove analog inputs
    * add external adc
    * remove dummy connectors
    * add D-Sub connectors
    [mainboard.sch, mainboard_microcontroller.sch, rxsm-event-lines.sch, rxsm-rs422.sch]
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2017-04-15 [powerboard] various fixes (charge circuit, boost converter, 5V buck regulator)
    [powerboard.sch, powerboard_battery_charging.sch, powerboard_regulator_28V-to-5V.sch, powerboard_stepup_24V.sch]
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2017-04-20 [powerboard] fixed motor controller sub-schematic wiring
    [powerboard.sch, powerboard_motor_controller.sch]
2017-04-20 [powerboard] fixed 5V buck regulator sub-schematic wiring
    [powerboard.sch, powerboard_regulator_28V-to-5V.sch]
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2017-04-26 boards/camera-light: fixed via connection problem, DRC without errors now
    [camera-light.kicad_pcb]
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2017-04-27 added solder-jumpers
    the clearance at the jumpers looks prettey small,
    is this allright?
    [temerature-sensor-DS1731.kicad_pcb, temerature-sensor-DS1731.sch]
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2017-05-04 board/pi: schematics: cleanup, bugfixing, added power LED and testpoints
    [pi-board.sch, stepdown_pi.sch]
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2017-05-07 schematics/pi: minor corrections, added annotation and most footprints
    [pi-board.sch, stepdown_pi.sch]
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2017-05-08 boards/temperature_sensor: reduced number of vias, corrected spelling error
    [temperature-sensor-DS1731.kicad_pcb, temperature-sensor-DS1731.sch]
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2017-05-09 schematics/pi: choose correct footprints for L and NMOS
    [pi-board.sch, stepdown_pi.sch]
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2017-05-12 [mainboard] first traces routed, some pins in schematic swapped
    [mainboard-LTC2984_1.sch, mainboard-LTC2984_2.sch, mainboard-LTC2984_3.sch, mainboard-LTC2984_4.sch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]
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2017-05-12 [mainboard] more traces routed, some pins swapped
    [mainboard.kicad_pcb, mainboard_microcontroller.sch]
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2017-06-13 boards/pi: fix net naming confusion, minor changes
    [pi-board.kicad_pcb, pi-board.sch, stepdown_pi.sch]
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2017-06-19 [lt3757-boost-converter] fix silk screen
    [lt3757-boost-converter.kicad_pcb]
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2017-06-21 [mainboard] fix µC PWM pinout and exchange power input inductor (XAL40xx)
    [mainboard.kicad_pcb, mainboard.sch, mainboard_microcontroller.sch]
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2017-06-27 [mainboard] fix d-sub connector placement
    [mainboard.kicad_pcb, mainboard.sch, mainboard_temp_sensors.sch]
2017-06-27 [powerboard] fix d-sub connector placement
    [heat-probes.sch, powerboard.kicad_pcb, powerboard.sch]
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2017-06-28 [mainboard] fix silkscreen
    [mainboard.kicad_pcb]
2017-06-28 [powerboard] fix rs-422 termination resistor placement
    [powerboard.kicad_pcb]
2017-06-29 wires: fixed boost converter wiring
    [wiring-diagram.sch]
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2017-06-29 boards/pi: minor corrections
    [pi-board.kicad_pcb]
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2017-07-01 [powerboard] cut upper left corner; two shorts fixed
    [powerboard.kicad_pcb]
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2017-07-01 [powerboard] replace heat probe D-Sub connector with screw terminals
    [heat-probes.sch, powerboard.kicad_pcb, powerboard.sch]
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2017-07-01 [powerboard] fix silkscreen and mask
    [powerboard.kicad_pcb]
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2017-07-10 [powerboard] fix DRC and export layout
    [powerboard.kicad_pcb]
2017-07-11 [powerboard] fix schematic label
    [powerboard.sch]
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2017-09-02 fix/ds1731: updated footprint and dimensions, pls check footprint
    [temperature-sensor-DS1731.kicad_pcb, temperature-sensor-DS1731.sch]
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2017-09-04 fix/ds1731: changed mounting hole to m2
    [temperature-sensor-DS1731.kicad_pcb]
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2017-09-28 fix/heds: updated the footprint of the heds9731#X50
    [optical-distance.kicad_pcb, optical-distance.sch]
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2017-10-25 addressed all the errors
    [iscaBottom.kicad_pcb, iscaBottom.sch, iscaBottom.step]
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2017-10-27 [CupolaFeedthrough] fix silkscreen
    [CupolaFeedthrough-B.Cu.gbl, CupolaFeedthrough-B.Mask.gbs, CupolaFeedthrough-B.SilkS.gbo, CupolaFeedthrough-Edge.Cuts.gm1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]
2017-10-28 [CupolaFeedthrough] fix board outline
    [CupolaFeedthrough-B.Cu.gbl, CupolaFeedthrough-B.Mask.gbs, CupolaFeedthrough-B.SilkS.gbo, CupolaFeedthrough-Edge.Cuts.gm1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]
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2017-10-30 fixes/wires: updated everything
    the high level diagram lost some visual appeal
    [wiring-diagram.sch]
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2017-11-05 [optical distance] fix GND connection
    [optical-distance.kicad_pcb]
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2017-11-16 [flir-board] fix board outline file name extension
    [flir-board-neu-2.dxf]
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2017-11-16 [optical-distance] export gerber correctly
    [optical-distance-B.Cu.gbl, optical-distance-B.Mask.gbs, optical-distance-B.SilkS.gbo, optical-distance-Edge.Cuts.gm1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]
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2017-11-17 pi-board: update pam footprint, fix ground plane / C4 bug
    [pi-board.kicad_pcb]
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2017-11-22 [powerboard] LTC4010: fix R and C values
    [powerboard_battery_charging.sch]
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2017-11-23 [powerboard] fix minor issues in all schematics; revision: rev10
    [heat-probes.sch, powerboard-led-driver.sch, powerboard.sch, powerboard_adc.sch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]
2017-11-23 [powerboard] fix some footprint assignments
    [heat-probes.sch, powerboard.sch, powerboard_motor_controller.sch]
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2017-11-27 [mainboard] fix D-Sub HD (26 and 44 pin)row spacing
    [mainboard.kicad_pcb]
2017-11-27 [mainboard] fix flash chip footprint
    [mainboard.kicad_pcb, mainboard_flash_1.sch, mainboard_flash_2.sch]
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2017-12-04 [powerboard] fix some component values
    [powerboard.sch, rxsm-rs422.sch]
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2018-01-05 ams5915v2: fixed permanently off max4995
    [ams5915v2.kicad_pcb, ams5915v2.sch]
2018-01-06 [lt3757-boost-converter] fix output voltage
    [lt3757.sch]
2018-01-07 ams5915x2: complete redesign. using leds to signal power, fault and 3v3. added pullup on fault line, fixed missing libs, fixed believed short
    [ams5915v2.kicad_pcb, ams5915v2.sch]
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2018-01-08 [ams5915v2] new board design: minor fixes
    [ams5915v2.kicad_pcb]
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2018-06-04 [board][HPPM-Rotation-Encoder-VarA] fix wrong pinout
    [HPPM-Rotation-Encoder-VarA.kicad_pcb, HPPM-Rotation-Encoder-VarA.sch]
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2019-01-06 [board][pixart-sensor] Fix sensor placement
    [pixart-sensor.kicad_pcb, pixart-sensor.sch]
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2019-01-15 [boards] Swap channels for layout, add second heat resistor
    [differential_drivers.sch]
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2019-01-15 cupola board: Swap STM pins for easier layout
    [stm32.sch]
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2019-01-16 [board][cupola-cable-board] Swap SWDIO and SWCLK pins
    [cupola-cable-board.kicad_pcb, stm32.sch]
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2019-01-17 [board][magnetic-distance] Place sensor chip correctly (on PCB front side)
    [magnetic-distance.kicad_pcb]
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2019-02-11 [cupola-feedthrouch-simulator] Fix DRC issues
    [cupola-feedthrouch-simulator.kicad_pcb]
2019-02-11 removed wrongly changed files
    [CupolaFeedthrough-2019-02-09-20-31-21.sch, heat-probes-2018-08-28-14-26-07.sch, powerboard-2018-08-28-14-26-07.sch, powerboard-led-driver-2018-08-28-14-26-07.s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]
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

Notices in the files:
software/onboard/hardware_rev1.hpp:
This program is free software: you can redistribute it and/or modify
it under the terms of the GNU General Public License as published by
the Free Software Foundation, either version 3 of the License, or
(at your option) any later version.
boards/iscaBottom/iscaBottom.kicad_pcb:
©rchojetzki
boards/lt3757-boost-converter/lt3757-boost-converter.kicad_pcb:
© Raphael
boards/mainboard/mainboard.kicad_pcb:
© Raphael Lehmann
